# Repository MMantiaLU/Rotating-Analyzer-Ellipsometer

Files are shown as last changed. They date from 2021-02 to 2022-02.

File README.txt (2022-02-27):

The folder "STEP Files" contains the .STEP-formatted 3D model files of the opto-mechanical componentry which construct the 3D-printed RAE. STEP files are widely compatible with CAD programs and can be used to analyze dimensions or make modifications to the components.

The folder "STL Files" contains the .STL-formatted stereolithographic files of the opto-mechanical componentry which construct the 3D-printed RAE. STL Files are ready to be imported into a "slicer" program (such as Ultimaker Cura) which converts them into GCODE files appropriate for 3D printing.

"Calibrating the Rotating Polarizer Mounts.pdf" is an instructional document which details two simple methods for calibrating 3D-printed rotating polarizer mounts. Two of these mounts are required for the RAE, one becoming the fixed polarizer, and one becoming the rotating analyzer. Calibration aligns the transmission angle of the polarizer with the plane of incidence and involves manually graduating the four critical angles (0, +45, 90, and -45) for use with the RAE.

"Constructing the 3D Printed RAE.pdf" is an instructional document which details the assembly of the 3D-printed RAE, including a list of parts both 3D printed and non-printed. Also provided at the end of the document is guidance for making custom "Light Source" and "Light Sensor" mounts.

"Ellipsometer Data Collection and Modeling.xlsx" is a Microsoft Excel document that allows one to experimentally determine thin film properties using intensity measurements collected with the 3D-printed RAE. Instructions on using the document are built-in to the first page. The model's regressive fitting process requires Excel's Solver add-on be enabled in the settings.

"Ellipsometry, Jesper Jung et al., Aalborg University (2004).pdf" is a copy of the "Ellipsometry" (Reference 9) project report obtained from <http://homes.nano.aau.dk/kp/Ellipsometry/main.pdf>. This report is included as a backup of the original source, as it contains valuable discussion and derivations for ellipsometric theory. Permission for redistribution was obtained by the authors.

"LICENSE.txt" contains a standard set of terms and conditions (CC BY-NC-SA 4.0) used to share work with public license. Under these terms:
*Attribution — You must give appropriate credit, provide a link to the license, and indicate if changes were made. You may do so in any reasonable manner, but not in any way that suggests the licensor endorses you or your use.
*NonCommercial — You may not use the material for commercial purposes.
*ShareAlike — If you remix, transform, or build upon the material, you must distribute your contributions under the same license as the original.
*No additional restrictions — You may not apply legal terms or technological measures that legally restrict others from doing anything the license permits.

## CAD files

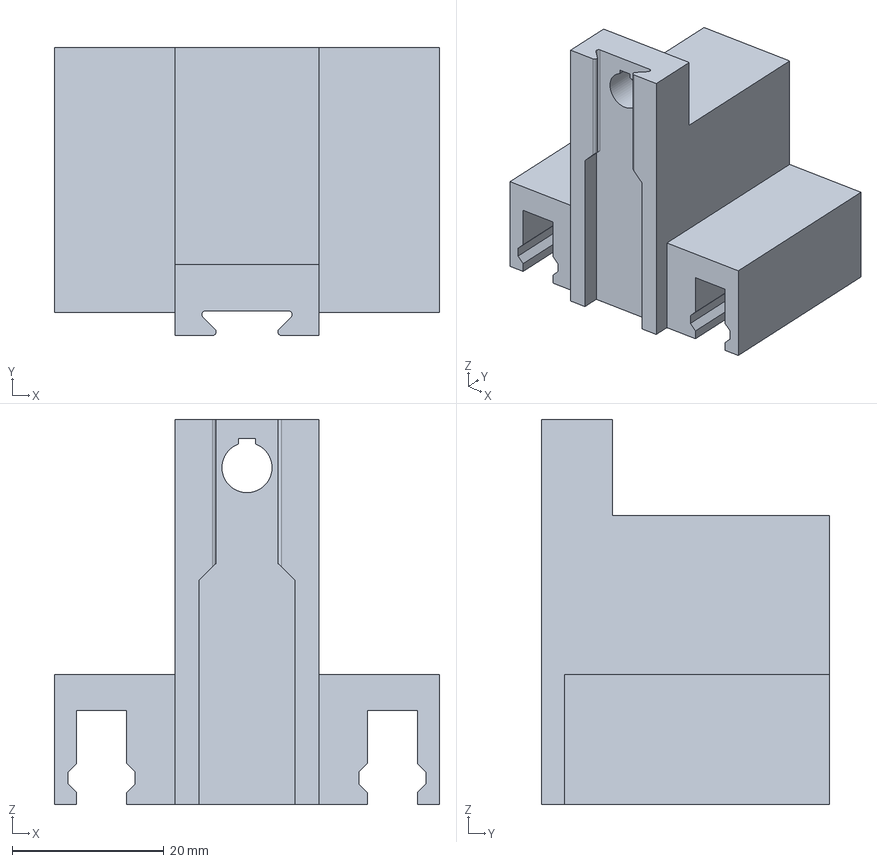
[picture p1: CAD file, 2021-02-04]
STEP Files/Linear Sample Mount Assembly/LSM Head.step
50.8 x 38.0 x 50.8 mm

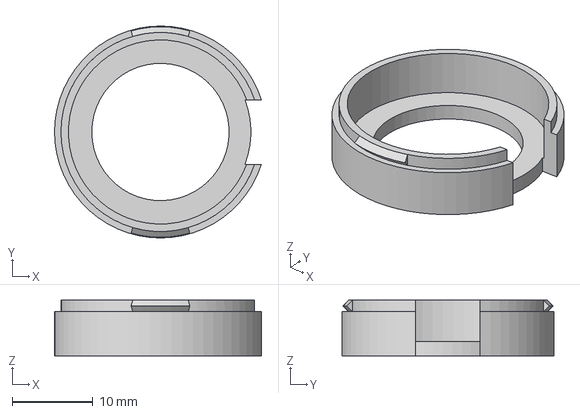
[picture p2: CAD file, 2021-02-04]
STEP Files/Rotating Polarizer Mount Assembly/RPM Cap.step
25.6 x 26.2 x 6.88 mm

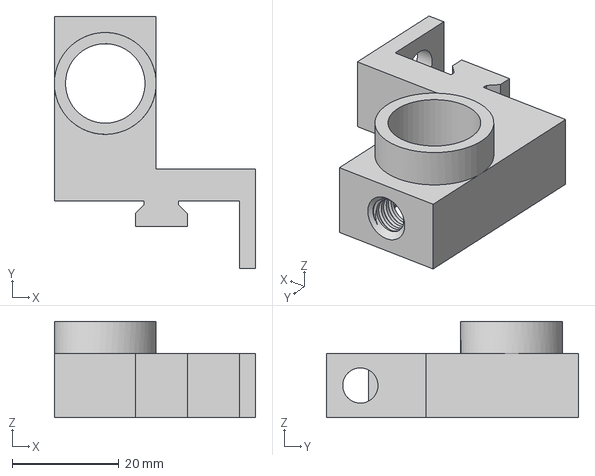
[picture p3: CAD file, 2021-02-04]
STEP Files/Vernier Light Sensor Mount.step
37.8 x 47.2 x 18.0 mm

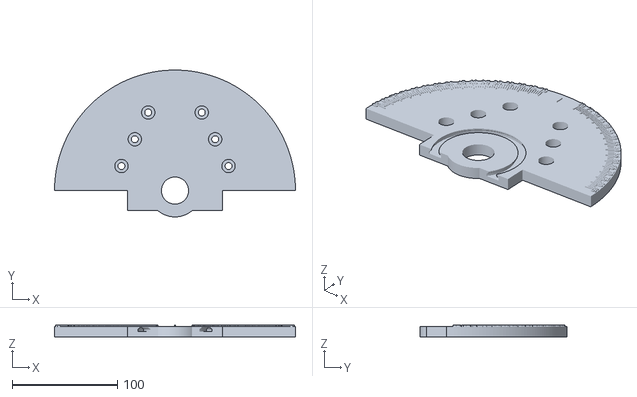
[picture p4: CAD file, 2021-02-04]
STL Files/Goniometer Assembly/Gonio Body.stl
228.6 x 139.3 x 11.0

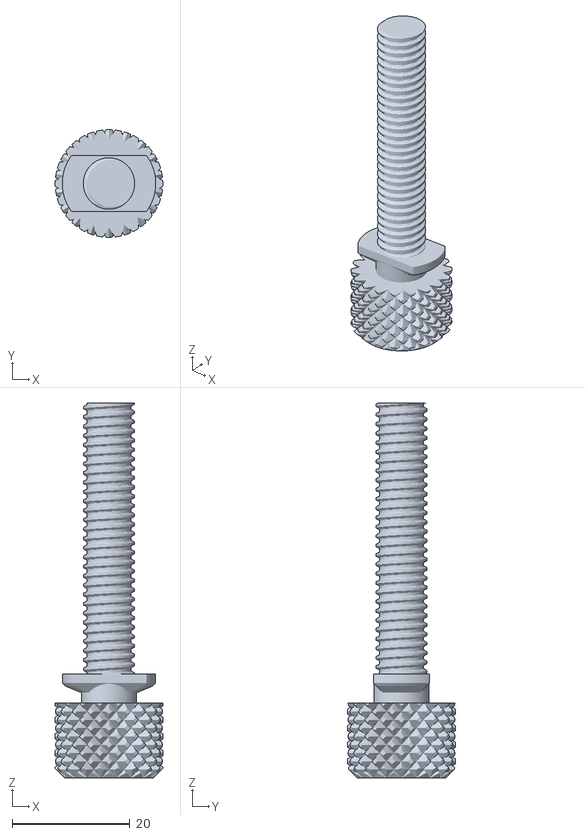
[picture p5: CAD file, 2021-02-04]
STL Files/Linear Sample Mount Assembly/LSM Drive.stl
18.3 x 18.3 x 63.7

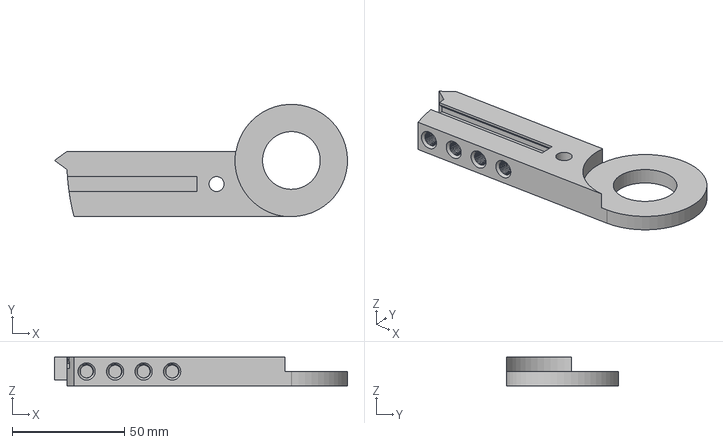
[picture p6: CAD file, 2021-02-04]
STEP Files/Goniometer Assembly/Gonio Arm (Left).step
130.5 x 50.0 x 12.7 mm

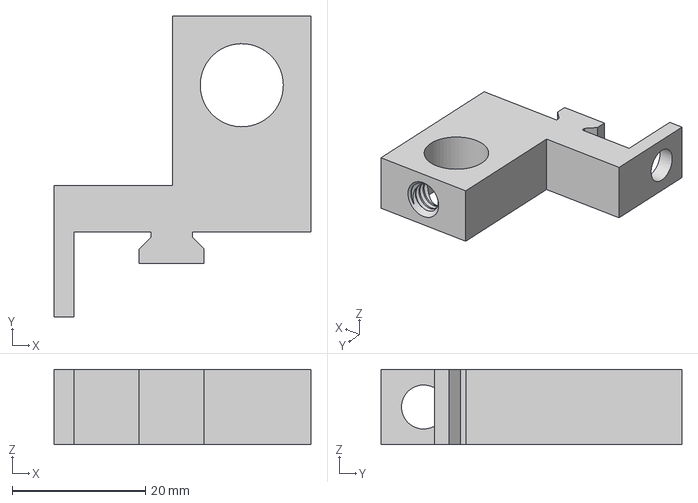
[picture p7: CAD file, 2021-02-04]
STEP Files/Laser Mount.step
38.5 x 45.1 x 11.3 mm

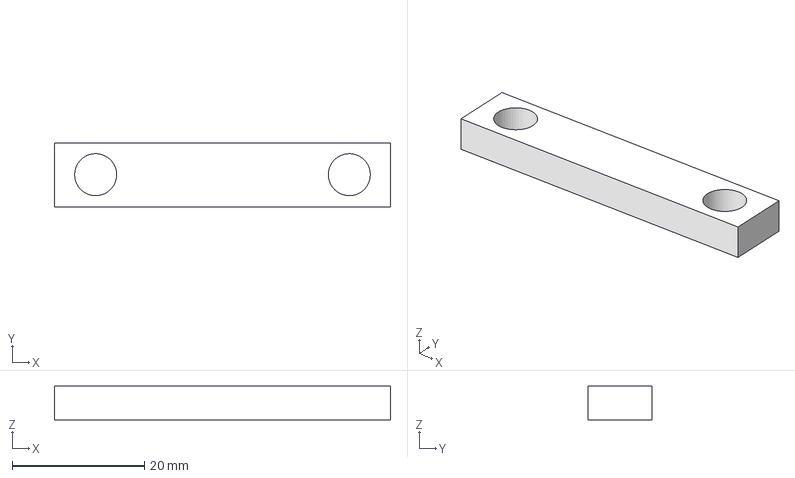
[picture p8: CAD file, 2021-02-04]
STEP Files/Linear Sample Mount Assembly/LSM Bar.step
50.8 x 9.63 x 5.08 mm

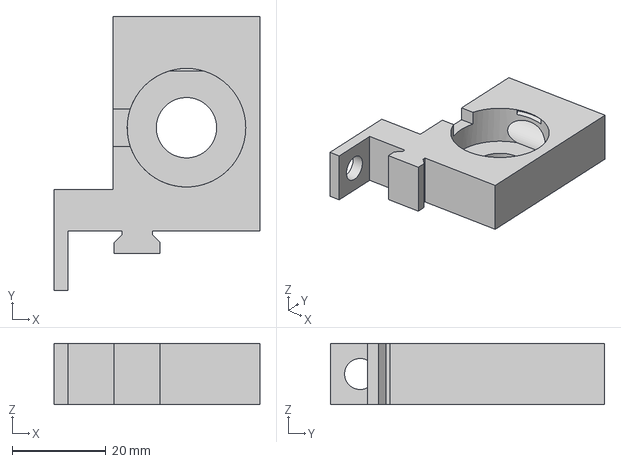
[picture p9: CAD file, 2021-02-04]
STEP Files/Rotating Polarizer Mount Assembly/RPM Body (Left).step
43.8 x 58.4 x 13.0 mm

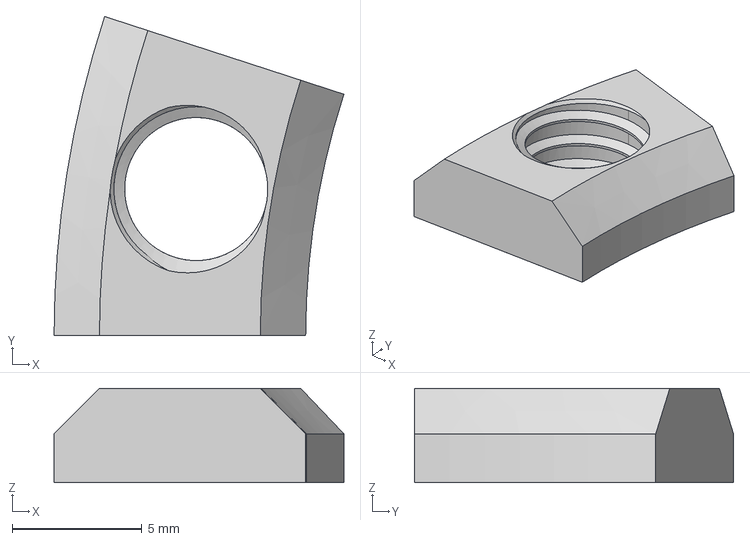
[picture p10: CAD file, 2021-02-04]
STEP Files/Goniometer Assembly/Gonio Rail.step
11.2 x 12.3 x 3.63 mm

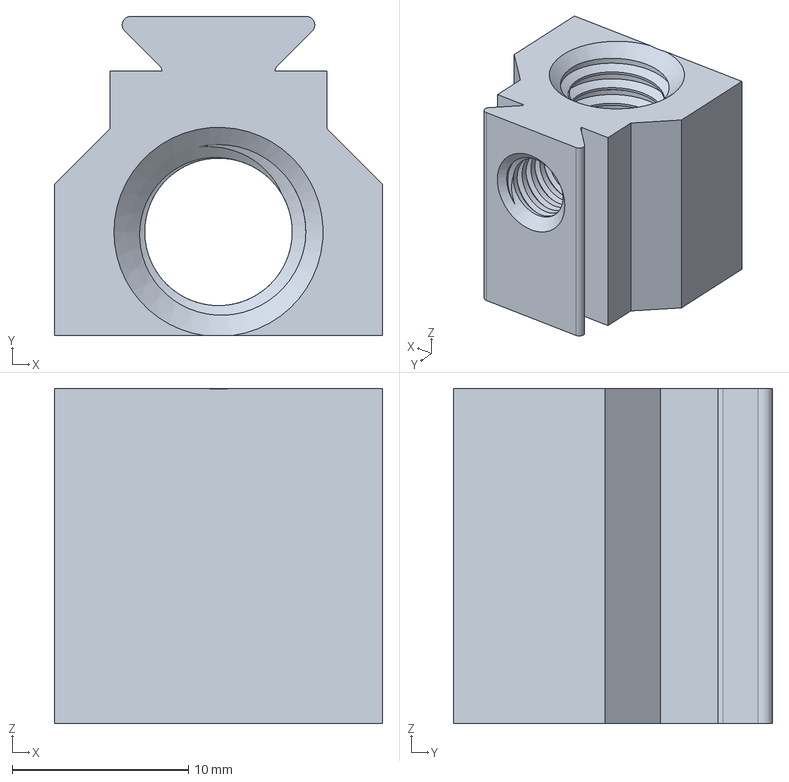
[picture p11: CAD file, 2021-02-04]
STEP Files/Linear Sample Mount Assembly/LSM Rail.step
18.7 x 18.1 x 19.1 mm

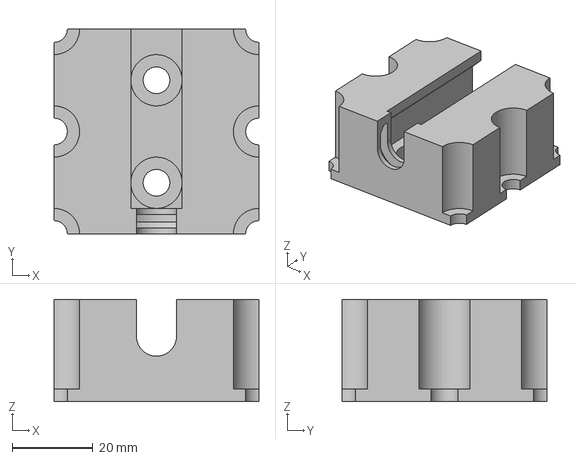
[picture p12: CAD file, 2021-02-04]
STEP Files/Linear Sample Mount Assembly/LSM Body.step
50.8 x 50.8 x 25.4 mm

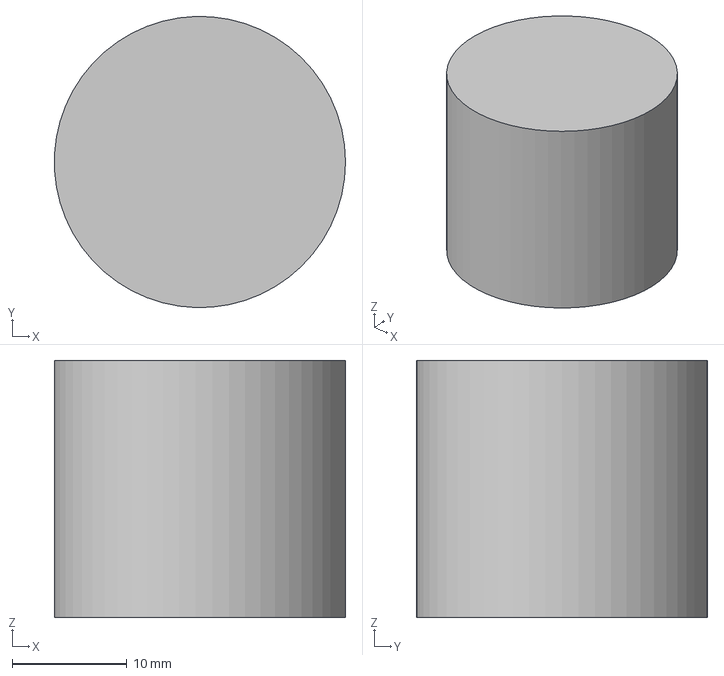
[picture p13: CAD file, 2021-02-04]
STEP Files/Goniometer Assembly/Gonio Arm Hinge Pin.step
25.4 x 25.4 x 22.5 mm

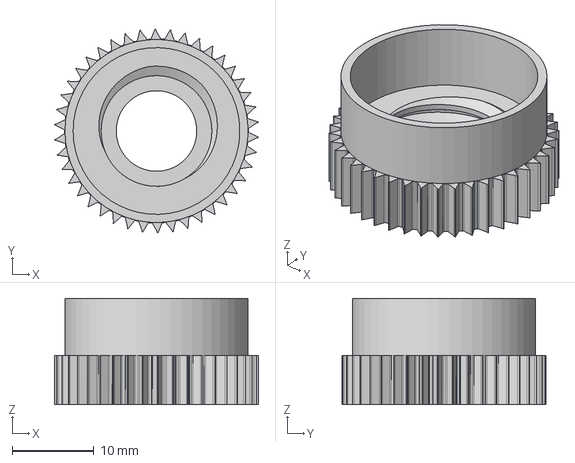
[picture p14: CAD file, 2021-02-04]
STEP Files/Rotating Polarizer Mount Assembly/RPM Gear-Optic Mount.step
25.0 x 25.0 x 13.0 mm

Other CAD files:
STEP Files/Rotating Polarizer Mount Assembly/RPM Body (Right).step
STEP Files/Goniometer Assembly/Gonio Arm (Right).step
STEP Files/Goniometer Assembly/Gonio Rail Screw.step
STEP Files/Rotating Polarizer Mount Assembly/RPM Optic Screw.step
STEP Files/Linear Sample Mount Assembly/LSM Nut.step
STEP Files/Linear Sample Mount Assembly/LSM Screw.step
STL Files/Goniometer Assembly/Gonio Arm (Left).stl
STL Files/Goniometer Assembly/Gonio Arm (Right).stl
STL Files/Goniometer Assembly/Gonio Arm Hinge Pin.stl
STL Files/Goniometer Assembly/Gonio Rail Screw.stl
STL Files/Goniometer Assembly/Gonio Rail.stl
STL Files/Laser Mount.stl
STL Files/Linear Sample Mount Assembly/LSM Bar.stl
STL Files/Linear Sample Mount Assembly/LSM Body.stl
STL Files/Linear Sample Mount Assembly/LSM Head.stl
STL Files/Linear Sample Mount Assembly/LSM Screw.stl
STL Files/Rotating Polarizer Mount Assembly/RPM Body (Left).stl
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

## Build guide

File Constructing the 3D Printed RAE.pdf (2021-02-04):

Constructing the 3D Printed Rotating Analyzer Ellipsometer

## Contents

## Parts List

3D Printed Parts
Goniometer
A. x1 Gonio Arm (Left)
B. x1 Gonio Arm (Right)
C. x1 Gonio Arm Hinge Pin
D. x1 Gonio Body
E. x2 Gonio Rail Screw
F. x2 Gonio Rail

Linear Sample Mount

A. x2 LSM Bar
B. x1 LSM Body
C. x1 LSM Drive
D. x1 LSM Head
E. x4 LSM Nut
F. x1 LSM Rail
G. x4 LSM Screw

Rotating Polarizer Mounts

A. x1 RPM Body (Left)
B. x1 RPM Body (Right)
C. x2 RPM Cap
D. x2 RPM Gear-Optic Mount
E. x2 RPM Optic Screw
F. x2 RPM Worm Drive

Laser Mount

Vernier Light Sensor Mount

Non-Printed Parts
x1 Laser, 653-nm, 3-5v, 5mW (https://www.amazon.com/gp/product/B072XF49LK/ref=ox_sc_act_title_2?smid=A30QSGOJR8LMXA&th=1)

x2 Polarizing Film, Linear (https://www.amazon.com/Polarizing-Film-Sheet-Gadget-Electronics/dp/B004X3XFHU)

x1 Vernier Light Sensor

x1 Vernier Go!Link

x1 Glass Slide (optional for RPM calibration)

x11 1/4"-20 x 3/8" cap head machine screw

## Assembly Instructions

Goniometer

### 1. The Gonio Body [D] can be fixed to a standard imperial optical bench by fastening

1/4"-20 machine screwsthrough any of the three sets of countersunk holes on the body.

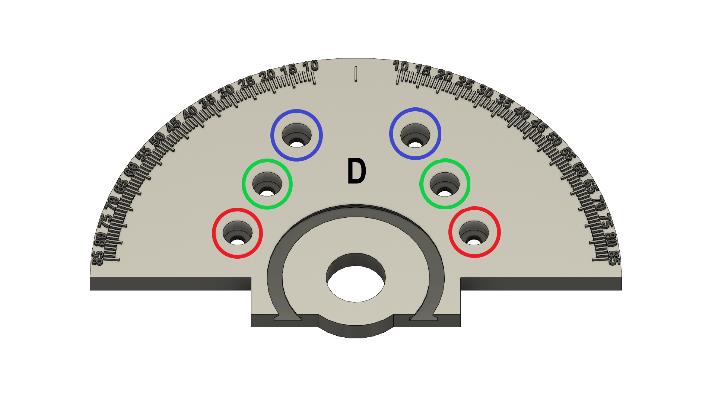
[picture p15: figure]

### 2. Gonio Arm (Left) [A] and Gonio Arm (Right) [B] are attached to the Gonio Body

[D] by sliding Gonio Arm Hinge Pin [C] into the holes at the pivot point of the goniometer arms.

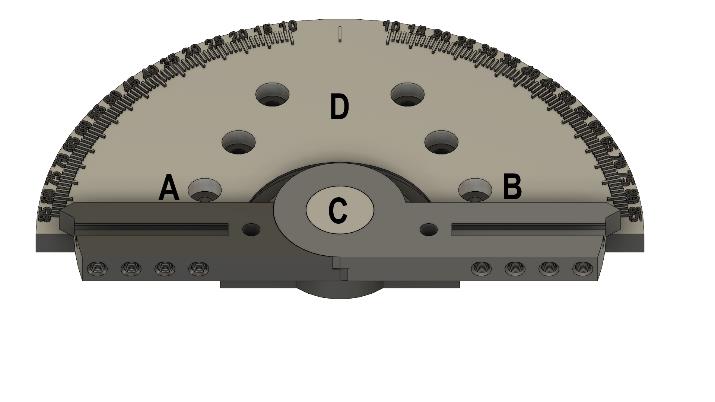
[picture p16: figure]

### 3. Slide the Gonio Rails [F] into the slots on both sides of the Gonio Body [D]. Gonio

Rail Screws [E] go through the vertical holes in the Gonio Arms [A,B]. The goniometer arms can be fixed at specified angles by tightening Gonio Rail Screw [E] into Gonio Rail [F], which clamps the arms to the goniometer body. Do not overtighten.

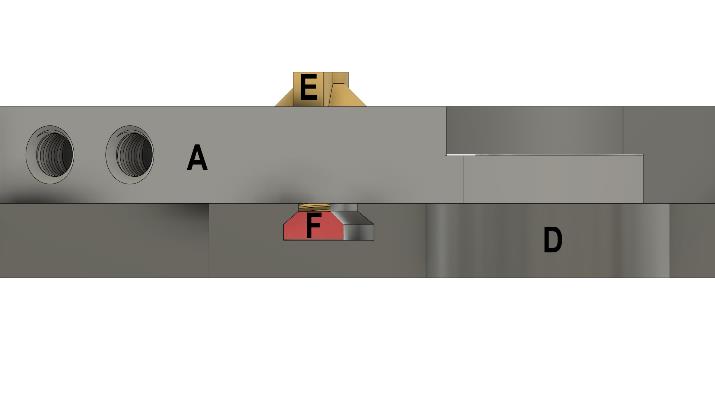
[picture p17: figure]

Linear Sample Mount

### 1. The LSM Drive [C] drops into the LSM Body [B] while the drive collar is oriented

vertical. Once Inside the body, the drive can rotate freely.

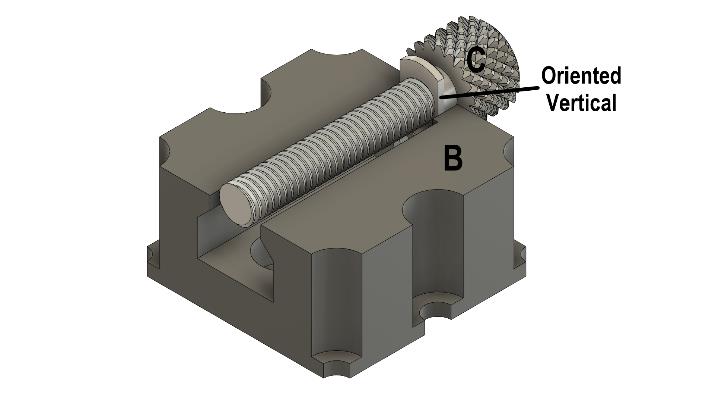
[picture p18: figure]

### 2. The LSM Rail [F] slides into the front of the LSM Body [B] and threads onto the

LSM Drive [C]. The threaded hole at the top of the LSM Rail [F]should be proximal to the LSM Drive [C].

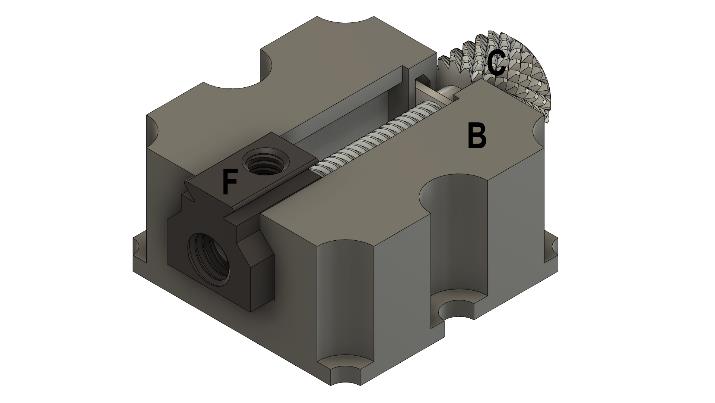
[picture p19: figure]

### 3. The LSM Body [B] should be mounted adjacent to the pivot point of the

goniometer arms prepared in the Goniometer assembly instructions. Various mounting areas on the LSM Body [B] can be used. At least two 1/4”-20 machine screws are recommended.

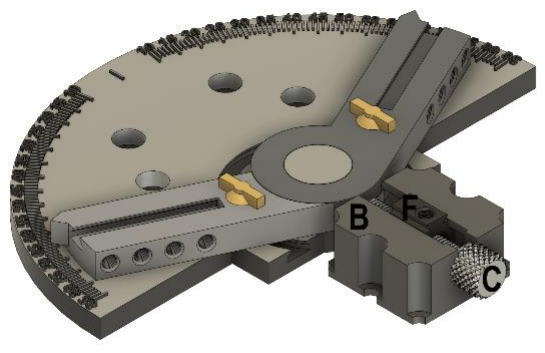
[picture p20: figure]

### 4. The LSM Head [D] slides onto the top of the LSM Rail [F] and is fastened with a

1/4”-20 machine screw.

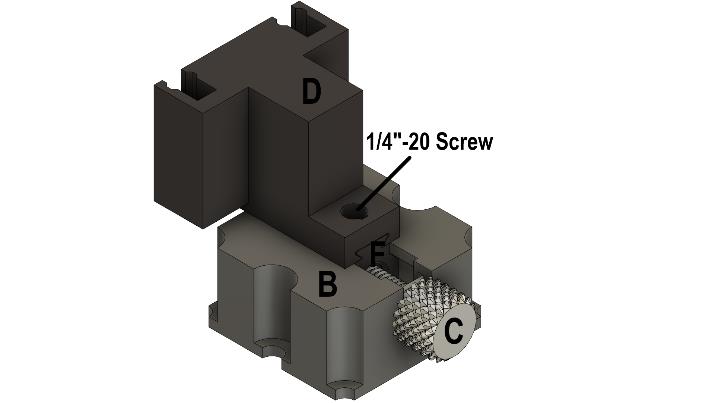
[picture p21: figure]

### 5. An LSM Bar [A] can be used to mount flat samples against the LSM Head [D]. The

bar has two holes which allow LSM Screws [G] through to thread into LSM Nuts [E] and provide a clamping force to the sample. One bar may be used, but two are recommended to fix both the top and bottom of a sample to the head.

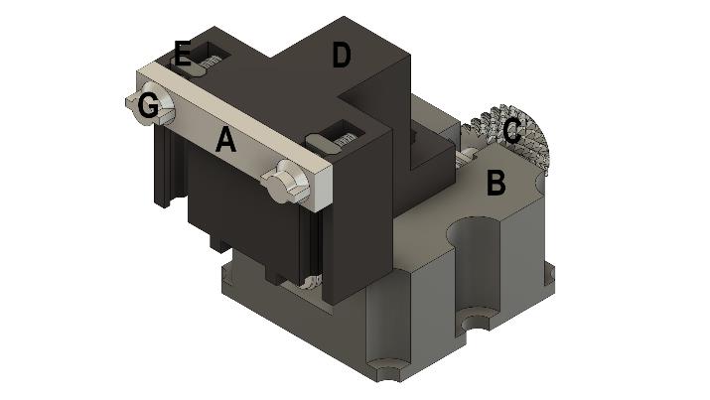
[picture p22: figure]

Rotating Polarizer Mounts

### 1. The RPM Worm Drive [F] is inserted into the hole at the top of the RPM Body

[A/B]. The worm drive should snap into place but freely rotate.

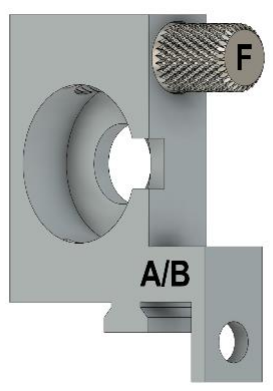
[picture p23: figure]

### 2. The RPM Gear-Optic Mount [D] drops into the front of the RPM Body [A/B]. The

internal area of the gear accepts a 0.5” diameter linear polarizer, which can be cut out from a larger sheet of polarizing film. An RPM Optic Screw [E] can be fastened into the internal threads of the RPM Gear-Optic Mount [D] to fix the internal linear polarizer in place.

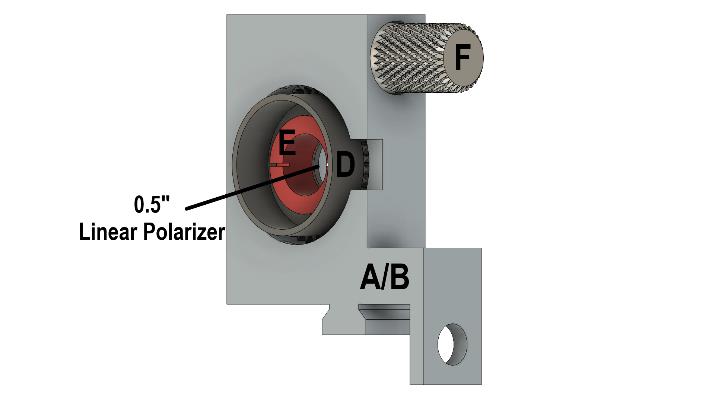
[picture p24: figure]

### 3. The RPM Cap [C] snaps into the RPM Body [A/B] if oriented so that the notches

in both components are aligned. This notched area of the RPM is used for scribing and reading marks that indicate the transmission axis of the internally mounted polarizer. See “Calibrating the Rotating Polarizer Mounts” for detailed instructions on that process.

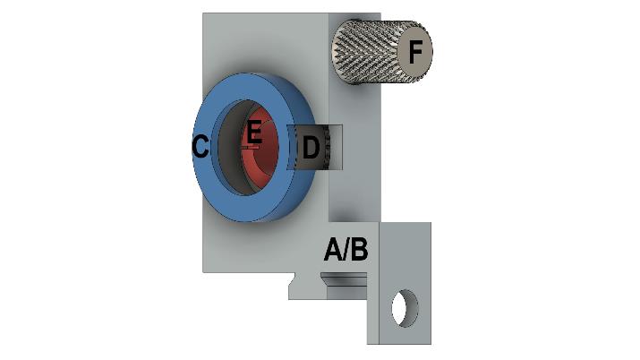
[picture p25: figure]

Mounting Optics to the Instrument
The light source, rotating polarizer mounts, and light intensity sensor should be mounted upon the pivoting goniometer arms of the instrument. Channels that run down the arms are intended to accept the matching rails at the bottom of these mounts. The threaded holes on the side the goniometer arms allow for fastening of the optical mounts with 1/4"-20 machine screws.

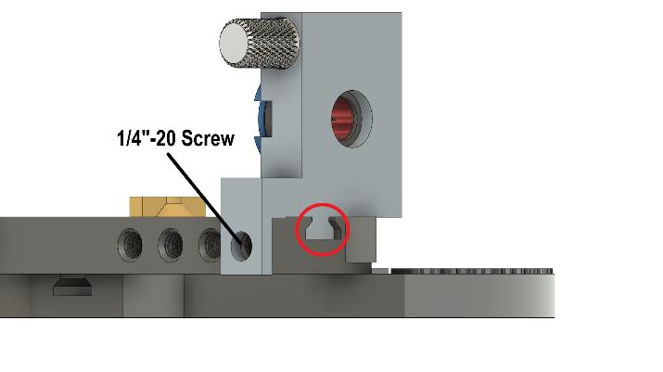
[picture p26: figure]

The included Laser Mount and Vernier Light Sensor Mount have large holes which the laser and sensor can slide into. A threaded hole at the top of these mounts accepts a 1/4"-20 screw to fasten the components into the mount.

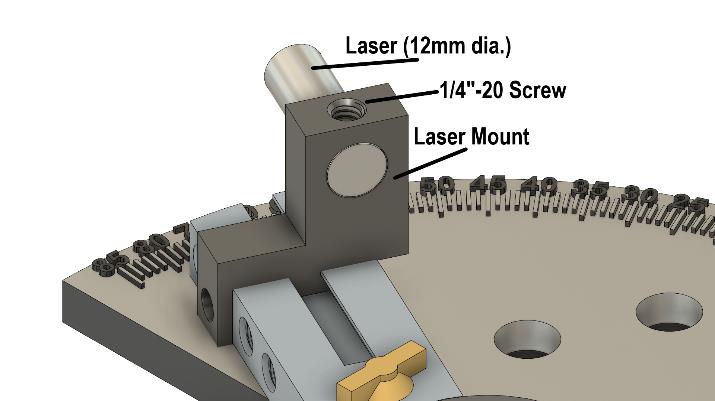
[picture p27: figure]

Custom Light Source and Light Sensor Mounts
If one desires to mount other light sources or light sensors to the instrument, they will be required to design and 3D print their own mounts. In this case, it is useful to know what parameters the other 3D printed components were designed with. Specifically, one would have to design their mount to be coincident with the optical path established by all the other components.

The Rotating Polarizer Mounts, Laser Mount, and Vernier Light Sensor Mount are designed to provide an optical axis that is 21.75-mm above the top surface of the Goniometer Arms and incurs reflection directly above the center of the Goniometer Arm Hinge Pin. The latter condition is critical for the goniometer’s function. This condition is met when the optical path is coincident with the indicator arrows at the ends of the Goniometer Arms, and when the sample surface is positioned above the central axis of the Goniometer Arm Hinge Pin using the Linear Sample Mount. A means of testing for these conditions involves sweeping of the goniometer arm with the mounted light source and looking for corresponding lateral movements of the position of the light “spot” on the sample surface. If the mounts are designed and fixed properly, and the sample is in the correct position, there should be no lateral movement of the spot. Elongation or shortening of the spot size at extreme goniometer angles of incidence is expected.

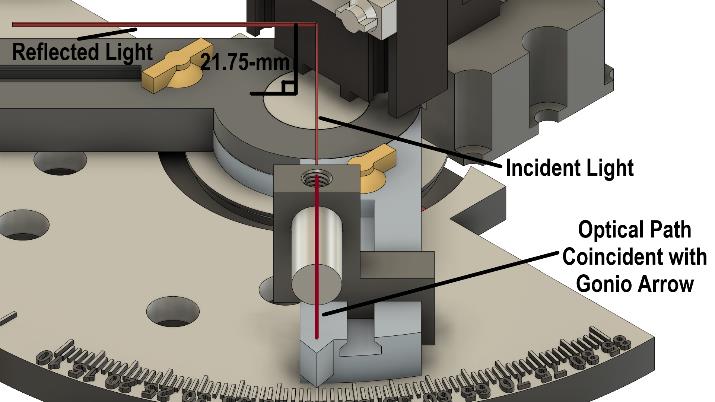
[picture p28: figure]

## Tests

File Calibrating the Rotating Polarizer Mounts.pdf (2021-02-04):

Calibrating the 3D Printed Rotating Polarizer Mounts

Calibration of the 3D printed rotating polarizer mount involves manually scribing azimuth angle graduations on the circular wall protruding from the gear in which a polarizer is mounted (Fig. 1). The critical polarizer element azimuth angles for use with the 3D printed RAE are 0, +45, 90, and – 45 degrees relative to the plane of incidence. The plane of incidence is perpendicular or normal to the sample surface, which is vertical when using the 3D printed linear sample mount (Fig. 2). The azimuth angles of 0 and 90 degrees are synonymous with the parallel
(p) and perpendicular (s) polarization planes respectively. The calibration of rotating polarizer mounts is outlined through two methods:

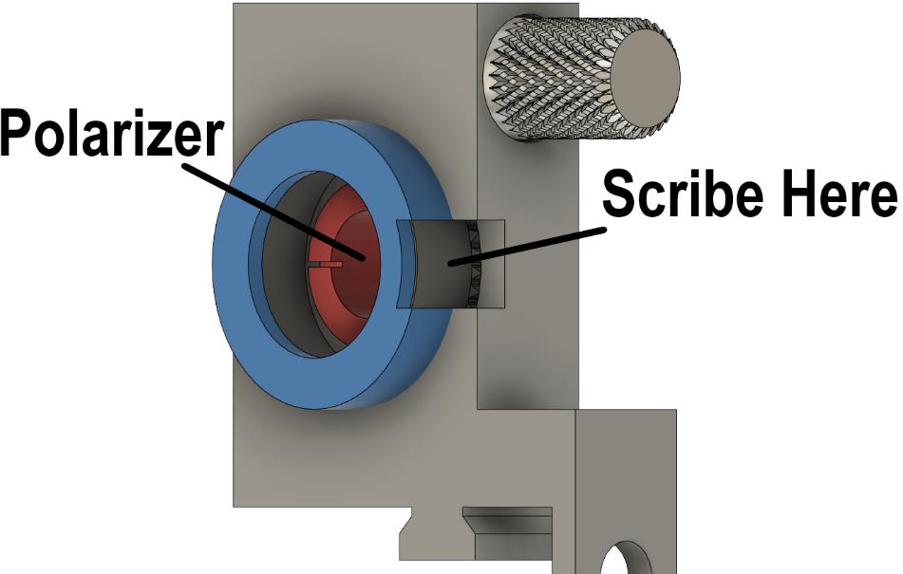
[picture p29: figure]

Figure 1 Rotating polarizer mount.

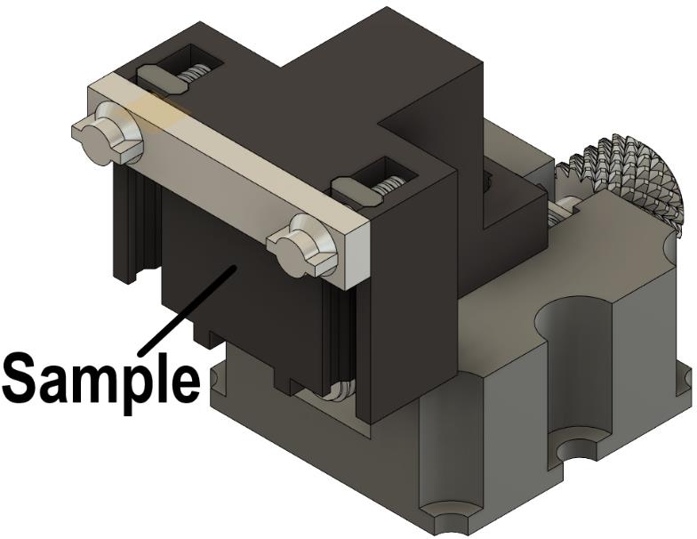
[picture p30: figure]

Figure 2. Linear sample mount.

Method 1) Use of a polarizer with known transmission axis:

One can determine the transmission axis of a polarizer by using another polarizer with a known transmission axis in a crossed polarizer configuration. Orient the known polarizer's transmission axis to be parallel (p) or perpendicular (s) to the instrument plane of incidence, and rotate the unknown polarizer until a null, or minimum light intensity, is measured by eye or a light sensor. At this azimuth angle, the unknown polarizer's axis of transmission is perpendicular to the known polarizer's axis of transmission. Repeat this process to determine both p and s orientations for the unknown polarizer.

Method 2) Use of a glass slide and the Brewster effect (Fig 3.):

One can calibrate the transmission axis of an unknown polarizer by reflecting light from a glass slide mounted in the linear sample mount of the 3D printed RAE. In this configuration, only one rotating polarizer mount is used in the instrument at a time, either the "polarizer" or "analyzer". Use the indices of refraction for glass (fused/amorphous SiO2) and the ambient (typically air) at the instrument's incident wavelength to calculate the Brewster angle using eq. 1.

θBrewster = atan (

nglass

nambient

)

Equation 1. Brewster angle.

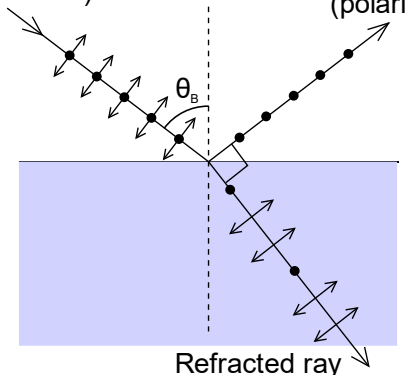
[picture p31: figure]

Figure 3. Diagram of the Brewster effect.

Set the RAE angle of incidence to the Brewster angle using the goniometer and reflect the instrument’s light source from the glass slide. Rotate the polarizer element until a null, or minimum light intensity, is measured by eye or a light sensor. At this azimuth angle, the polarizer’s axis of transmission is parallel to the plane of incidence. Repeat these steps with the other rotating polarization mount, and then use them together with method 1 to determine s orientations for both polarizers.

The +45 and – 45 degree polarizer azimuth angles can be estimated by using a protractor indexed against the previously determined p (0 degree) and s (90 degree) orientations scribed on the rotating mount.

The calibration of both the “polarizer” and “analyzer” elements can be checked against eachother by verifying that transmitted light intensity is minimized under a crossed polarizer configuration for all scribed azimuth angles.
